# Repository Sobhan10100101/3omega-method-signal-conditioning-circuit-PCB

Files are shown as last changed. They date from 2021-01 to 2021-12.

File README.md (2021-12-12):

3ω method is the most accurate method to investigate the thermal properties of thin films and bulk materials. Howerver, detection of small voltage variation at the third harmonic needs appropriate signal conditioning circuit to:

1. eliminate the 1st harmonic voltage from the responses which can overload the inputs of the lock-in amplifier
2. Amplify the signals before transferring with long cables to prevent distortion 

A simplified schematic diagram is depicted here:


The detailed description of the circuit and implementation of the experiment is published as **Determination of thermal conductivity, thermal diffusivity and specific heat capacity of porous silicon thin films using the 3ω method** which can be found here: https://authors.elsevier.com/a/1eD-044xa8rMx

Here you can find the image of the final PCB:
BlueBird

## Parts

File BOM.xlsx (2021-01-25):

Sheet: Sheet1
Partlist exported from C:/OneDrive - The University of Western Australia/PhD/13 - PCB/3-BlueBird/BlueBird_Sch.sch at 6/07/2020 12:08 PM
Part Value Device Package Description ALLIED_NUMBER CATEGORY DESCRIPTION HEIGHT MANUFACTURER MANUFACTURER_NAME MANUFACTURER_PART_NUMBER MPN OPERATING_TEMP PART_STATUS ROHS_COMPLIANT RS_PART_NUMBER RS_PRICE-STOCK SERIES SUB-CATEGORY THERMALLOSS TYPE VALUE VOLTAGE_RATING
C1 0.1uF C_CHIP-0805(2012-METRIC) CAPC2012X110 Capacitor - Generic Capacitor
C2 0.01uF C_CHIP-0805(2012-METRIC) CAPC2012X110 Capacitor - Generic Capacitor
C3 TAJC225M035RNJ TAJC225M035RNJ CAPPM6032X280N Tantalum Capacitors - Solid SMD 35volts 2.2uF 20% Tantalum Capacitors - Solid SMD 35volts 2.2uF 20% 2.8mm AVX TAJC225M035RNJ 1364458P http://uk.rs-online.com/web/p/products/1364458P
C4 TAJC225M035RNJ TAJC225M035RNJ CAPPM6032X280N Tantalum Capacitors - Solid SMD 35volts 2.2uF 20% Tantalum Capacitors - Solid SMD 35volts 2.2uF 20% 2.8mm AVX TAJC225M035RNJ 1364458P http://uk.rs-online.com/web/p/products/1364458P
C5 TMCUB1V105KTRF TMCUB1V105KTRF CAPPM3528X120N Cap Tant Solid 1uF 35V UB CASE 10% (3.5 X 2.8 X 1.2mm) Inward L SMD 3528-12 8.8 Ohm 125C T/R Cap Tant Solid 1uF 35V UB CASE 10% (3.5 X 2.8 X 1.2mm) Inward L SMD 3528-12 8.8 Ohm 125C T/R 1.2mm Vishay TMCUB1V105KTRF 1882061 http://uk.rs-online.com/web/p/products/1882061
C6 TMCUB1V105KTRF TMCUB1V105KTRF CAPPM3528X120N Cap Tant Solid 1uF 35V UB CASE 10% (3.5 X 2.8 X 1.2mm) Inward L SMD 3528-12 8.8 Ohm 125C T/R Cap Tant Solid 1uF 35V UB CASE 10% (3.5 X 2.8 X 1.2mm) Inward L SMD 3528-12 8.8 Ohm 125C T/R 1.2mm Vishay TMCUB1V105KTRF 1882061 http://uk.rs-online.com/web/p/products/1882061
C7 0.1uF C_CHIP-0805(2012-METRIC) CAPC2012X110 Capacitor - Generic Capacitor
C8 0.1uF C_CHIP-0805(2012-METRIC) CAPC2012X110 Capacitor - Generic Capacitor
C9 0.01uF C_CHIP-0805(2012-METRIC) CAPC2012X110 Capacitor - Generic Capacitor
C10 0.1uF C_CHIP-0805(2012-METRIC) CAPC2012X110 Capacitor - Generic Capacitor
C11 0.1uF C_CHIP-0805(2012-METRIC) CAPC2012X110 Capacitor - Generic Capacitor
C12 0.1uF C_CHIP-0805(2012-METRIC) CAPC2012X110 Capacitor - Generic Capacitor
F1 0458001.DR 0458001.DR FUSC3215X58N LITTELFUSE - 0458001.DR - Fuse, Surface Mount, 1 A, 48 VAC, 63 VDC, Very Fast Acting, 1206 LITTELFUSE - 0458001.DR - Fuse, Surface Mount, 1 A, 48 VAC, 63 VDC, Very Fast Acting, 1206 0.58mm LITTELFUSE 0458001.DR
F2 0458001.DR 0458001.DR FUSC3215X58N LITTELFUSE - 0458001.DR - Fuse, Surface Mount, 1 A, 48 VAC, 63 VDC, Very Fast Acting, 1206 LITTELFUSE - 0458001.DR - Fuse, Surface Mount, 1 A, 48 VAC, 63 VDC, Very Fast Acting, 1206 0.58mm LITTELFUSE 0458001.DR
IC1 OPA2277PA OPA2277PA DIP794W53P254L959H508Q8N Dual precision op-amp,OPA2277PA DIP8 Texas Instruments OPA2277PA, Dual Op Amp, 1MHz, 8-Pin PDIP Dual precision op-amp,OPA2277PA DIP8 Texas Instruments OPA2277PA, Dual Op Amp, 1MHz, 8-Pin PDIP 5.08mm Texas Instruments OPA2277PA 3071673P http://uk.rs-online.com/web/p/products/3071673P
IC2 L7809CV L7809CV TO255P460X1020X2008-3P Standard Regulator 9V 1.5A STMicroelectronics L7809CV, Single Linear Voltage Regulator, 1.5A 9 V, 2%, 3-Pin TO-220 70013895 Standard Regulator 9V 1.5A STMicroelectronics L7809CV, Single Linear Voltage Regulator, 1.5A 9 V, 2%, 3-Pin TO-220 4.6mm STMicroelectronics L7809CV 7140666P http://uk.rs-online.com/web/p/products/7140666P
IC3 KA7909TU KA7909TU TO254P470X1016X2019-3P ON Semiconductor, -9 V Linear Voltage Regulator, 1A, 1-Channel Negative, +/-4% 3-Pin, TO-220 KA7909TU ON Semiconductor, -9 V Linear Voltage Regulator, 1A, 1-Channel Negative, +/-4% 3-Pin, TO-220 KA7909TU 4.7mm ON Semiconductor KA7909TU 7390552P http://uk.rs-online.com/web/p/products/7390552P
IC4 OPA2277PA OPA2277PA DIP794W53P254L959H508Q8N Dual precision op-amp,OPA2277PA DIP8 Texas Instruments OPA2277PA, Dual Op Amp, 1MHz, 8-Pin PDIP Dual precision op-amp,OPA2277PA DIP8 Texas Instruments OPA2277PA, Dual Op Amp, 1MHz, 8-Pin PDIP 5.08mm Texas Instruments OPA2277PA 3071673P http://uk.rs-online.com/web/p/products/3071673P
IC5 OPA2277PA OPA2277PA DIP794W53P254L959H508Q8N Dual precision op-amp,OPA2277PA DIP8 Texas Instruments OPA2277PA, Dual Op Amp, 1MHz, 8-Pin PDIP Dual precision op-amp,OPA2277PA DIP8 Texas Instruments OPA2277PA, Dual Op Amp, 1MHz, 8-Pin PDIP 5.08mm Texas Instruments OPA2277PA 3071673P http://uk.rs-online.com/web/p/products/3071673P
J1 790-1098 790-1098 7901098 2 Way PCB Terminal Strip 2 Way PCB Terminal Strip 8.5mm RS Components 790-1098
J2 790-1098 790-1098 7901098 2 Way PCB Terminal Strip 2 Way PCB Terminal Strip 8.5mm RS Components 790-1098
J3 790-1098 790-1098 7901098 2 Way PCB Terminal Strip 2 Way PCB Terminal Strip 8.5mm RS Components 790-1098
J4 790-1098 790-1098 7901098 2 Way PCB Terminal Strip 2 Way PCB Terminal Strip 8.5mm RS Components 790-1098
J5 790-1098 790-1098 7901098 2 Way PCB Terminal Strip 2 Way PCB Terminal Strip 8.5mm RS Components 790-1098
J6 1729034 1729034 SHDR4W110P0X500_1X4_2000X810X1 Low profile PCB terminal block,5mm,4 way Phoenix Contact COMBICON MKDSN Series 5mm Pitch Straight PCB Terminal Block with Screw Termination, Through Hole, 4 Way 70054377 Low profile PCB terminal block,5mm,4 way Phoenix Contact COMBICON MKDSN Series 5mm Pitch Straight PCB Terminal Block with Screw Termination, Through Hole, 4 Way 10mm Phoenix Contact 1729034 8020620 http://uk.rs-online.com/web/p/products/8020620
J7 1729034 1729034 SHDR4W110P0X500_1X4_2000X810X1 Low profile PCB terminal block,5mm,4 way Phoenix Contact COMBICON MKDSN Series 5mm Pitch Straight PCB Terminal Block with Screw Termination, Through Hole, 4 Way 70054377 Low profile PCB terminal block,5mm,4 way Phoenix Contact COMBICON MKDSN Series 5mm Pitch Straight PCB Terminal Block with Screw Termination, Through Hole, 4 Way 10mm Phoenix Contact 1729034 8020620 http://uk.rs-online.com/web/p/products/8020620
J8 790-1098 790-1098 7901098 2 Way PCB Terminal Strip 2 Way PCB Terminal Strip 8.5mm RS Components 790-1098
J9 790-1098 790-1098 7901098 2 Way PCB Terminal Strip 2 Way PCB Terminal Strip 8.5mm RS Components 790-1098
J10 790-1098 790-1098 7901098 2 Way PCB Terminal Strip 2 Way PCB Terminal Strip 8.5mm RS Components 790-1098
J11 790-1098 790-1098 7901098 2 Way PCB Terminal Strip 2 Way PCB Terminal Strip 8.5mm RS Components 790-1098
J12 R25-3001602 R25-3001602 R253001602 Standoffs & Spacers M2.5 x 16mm HEX M/F BRASS 4.9mm A/F Standoffs & Spacers M2.5 x 16mm HEX M/F BRASS 4.9mm A/F 16mm Harwin R25-3001602
J13 R25-3001602 R25-3001602 R253001602 Standoffs & Spacers M2.5 x 16mm HEX M/F BRASS 4.9mm A/F Standoffs & Spacers M2.5 x 16mm HEX M/F BRASS 4.9mm A/F 16mm Harwin R25-3001602
J14 R25-3001602 R25-3001602 R253001602 Standoffs & Spacers M2.5 x 16mm HEX M/F BRASS 4.9mm A/F Standoffs & Spacers M2.5 x 16mm HEX M/F BRASS 4.9mm A/F 16mm Harwin R25-3001602
L1 MPZ2012S331AT000 MPZ2012S331AT000 INDC2012X105N Ferrite Beads Multi-Layer Power 330Ohm 25% 100MHz 2.5A 50mOhm DCR 0805 T/R Ferrite Beads Multi-Layer Power 330Ohm 25% 100MHz 2.5A 50mOhm DCR 0805 T/R 1.05mm TDK MPZ2012S331AT000
L2 MPZ2012S331AT000 MPZ2012S331AT000 INDC2012X105N Ferrite Beads Multi-Layer Power 330Ohm 25% 100MHz 2.5A 50mOhm DCR 0805 T/R Ferrite Beads Multi-Layer Power 330Ohm 25% 100MHz 2.5A 50mOhm DCR 0805 T/R 1.05mm TDK MPZ2012S331AT000
L3 MPZ2012S331AT000 MPZ2012S331AT000 INDC2012X105N Ferrite Beads Multi-Layer Power 330Ohm 25% 100MHz 2.5A 50mOhm DCR 0805 T/R Ferrite Beads Multi-Layer Power 330Ohm 25% 100MHz 2.5A 50mOhm DCR 0805 T/R 1.05mm TDK MPZ2012S331AT000
L4 MPZ2012S331AT000 MPZ2012S331AT000 INDC2012X105N Ferrite Beads Multi-Layer Power 330Ohm 25% 100MHz 2.5A 50mOhm DCR 0805 T/R Ferrite Beads Multi-Layer Power 330Ohm 25% 100MHz 2.5A 50mOhm DCR 0805 T/R 1.05mm TDK MPZ2012S331AT000
L5 MPZ2012S331AT000 MPZ2012S331AT000 INDC2012X105N Ferrite Beads Multi-Layer Power 330Ohm 25% 100MHz 2.5A 50mOhm DCR 0805 T/R Ferrite Beads Multi-Layer Power 330Ohm 25% 100MHz 2.5A 50mOhm DCR 0805 T/R 1.05mm TDK MPZ2012S331AT000
L6 MPZ2012S331AT000 MPZ2012S331AT000 INDC2012X105N Ferrite Beads Multi-Layer Power 330Ohm 25% 100MHz 2.5A 50mOhm DCR 0805 T/R Ferrite Beads Multi-Layer Power 330Ohm 25% 100MHz 2.5A 50mOhm DCR 0805 T/R 1.05mm TDK MPZ2012S331AT000
LED1 LS_R976 LS_R976 LEDC2012X40N Red 0805 CHIPLED LS R976N-R102 Osram Opto LS R976, CHIPLED 0805 Series Red LED, 633 nm, 2012 (0805), Rectangle Lens SMD Package Red 0805 CHIPLED LS R976N-R102 Osram Opto LS R976, CHIPLED 0805 Series Red LED, 633 nm, 2012 (0805), Rectangle Lens SMD Package 0.4mm OSRAM LS R976 4974804P http://uk.rs-online.com/web/p/products/4974804P
LED2 LS_R976 LS_R976 LEDC2012X40N Red 0805 CHIPLED LS R976N-R102 Osram Opto LS R976, CHIPLED 0805 Series Red LED, 633 nm, 2012 (0805), Rectangle Lens SMD Package Red 0805 CHIPLED LS R976N-R102 Osram Opto LS R976, CHIPLED 0805 Series Red LED, 633 nm, 2012 (0805), Rectangle Lens SMD Package 0.4mm OSRAM LS R976 4974804P http://uk.rs-online.com/web/p/products/4974804P
R1 10K R-US_R0402 R0402 RESISTOR, American symbol
R2 10K R-US_R0402 R0402 RESISTOR, American symbol
R3 10K R-US_R0402 R0402 RESISTOR, American symbol
R4 10K R-US_R0402 R0402 RESISTOR, American symbol
R5 10K R-US_R0402 R0402 RESISTOR, American symbol
R6 10K R-US_R0402 R0402 RESISTOR, American symbol
R7 10K R-US_R0402 R0402 RESISTOR, American symbol
R8 10K R-US_R0402 R0402 RESISTOR, American symbol
R9 5.6K R-US_R0402 R0402 RESISTOR, American symbol
R10 5.6K R-US_R0402 R0402 RESISTOR, American symbol
R11 200 R-US_R0402 R0402 RESISTOR, American symbol
R12 10K R-US_R0402 R0402 RESISTOR, American symbol
R13 10K R-US_R0402 R0402 RESISTOR, American symbol
R14 10K R-US_R0402 R0402 RESISTOR, American symbol
R15 10K R-US_R0402 R0402 RESISTOR, American symbol
R16 10K R-US_R0402 R0402 RESISTOR, American symbol
R17 100 R-US_R0402 R0402 RESISTOR, American symbol
R18 10K R-US_R0402 R0402 RESISTOR, American symbol
R19 50K R-US_R0402 R0402 RESISTOR, American symbol
R20 10K R-US_R0402 R0402 RESISTOR, American symbol
R21 100K R-US_R0402 R0402 RESISTOR, American symbol
R22 100K R-US_R0402 R0402 RESISTOR, American symbol
R23 10K R-US_R0402 R0402 RESISTOR, American symbol
R24 10K R-US_R0402 R0402 RESISTOR, American symbol
R25 10K R-US_R0402 R0402 RESISTOR, American symbol
R26 100K R-US_R0402 R0402 RESISTOR, American symbol
R27 100K R-US_R0402 R0402 RESISTOR, American symbol

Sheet: Sheet2
Parts | comment | Values | Type | Mfr. Part No. | RS Part number | Needed X | Order
Capacitors |  | 0.1 uF | Ceramic |  | 264-4416 | 6 | 25
Capacitors |  | 0.01 uF | Ceramic |  | 298-9309 | 2 | 25
Capacitors |  | 2.2µF | Tantalum |  | 136-4445 | 2 | 20
Capacitors |  | 1uF | Tantalum |  | 188-2380 | 2 | 10
Resistor |  | 0 | 1% |  | 740-9066 | 10 | 50
Resistor |  | 10K | 0.10% |  | 638-0532 | 18 | 50
Resistor |  | 5.6K | 1% |  | 678-9475 | 2 | 50
Resistor |  | 50K | 1% |  | 566-301 | 1 | 5
Resistor |  | 100K | 1% |  | 391-5719 | 3 | 10
Fuse |  |  |  |  | 174-0666 | 2
Ferit Bead |  |  |  |  | 724-1532 | 6 | 25
LED |  | Red |  |  | 497-4804 | 2 | 5
Standoff |  | 2.5M | Male to Female |  | 176-8401 (https://au.rs-online.com/web/p/standoffs/1768401/) | 3 | 10
Washer |  | 2.5M |  |  | 528-160 (https://au.rs-online.com/web/p/tap-washers/0528160/) | 3 | 50
Nut |  | 2.5M |  |  | 122-4399 (https://au.rs-online.com/web/p/hex-nuts/1224399/) | 3 | 50
Spacer |  | M3 |  |  | 102-6384
Terminal |  | 2Way |  |  | 790-1098 | 9 | 5
Terminal |  | 4Way |  | 282836-4 | 361-7689 | 2 | 5
Regulators |  | 9 Volt |  |  | 516-4812 | 1 | 10
Regulators |  | Negative 9 Volt |  |  | 697-4370 | 1 | 5
BNC Connector |  |  |  |  | 512-1225 | 2 | 3
POT1
POT2

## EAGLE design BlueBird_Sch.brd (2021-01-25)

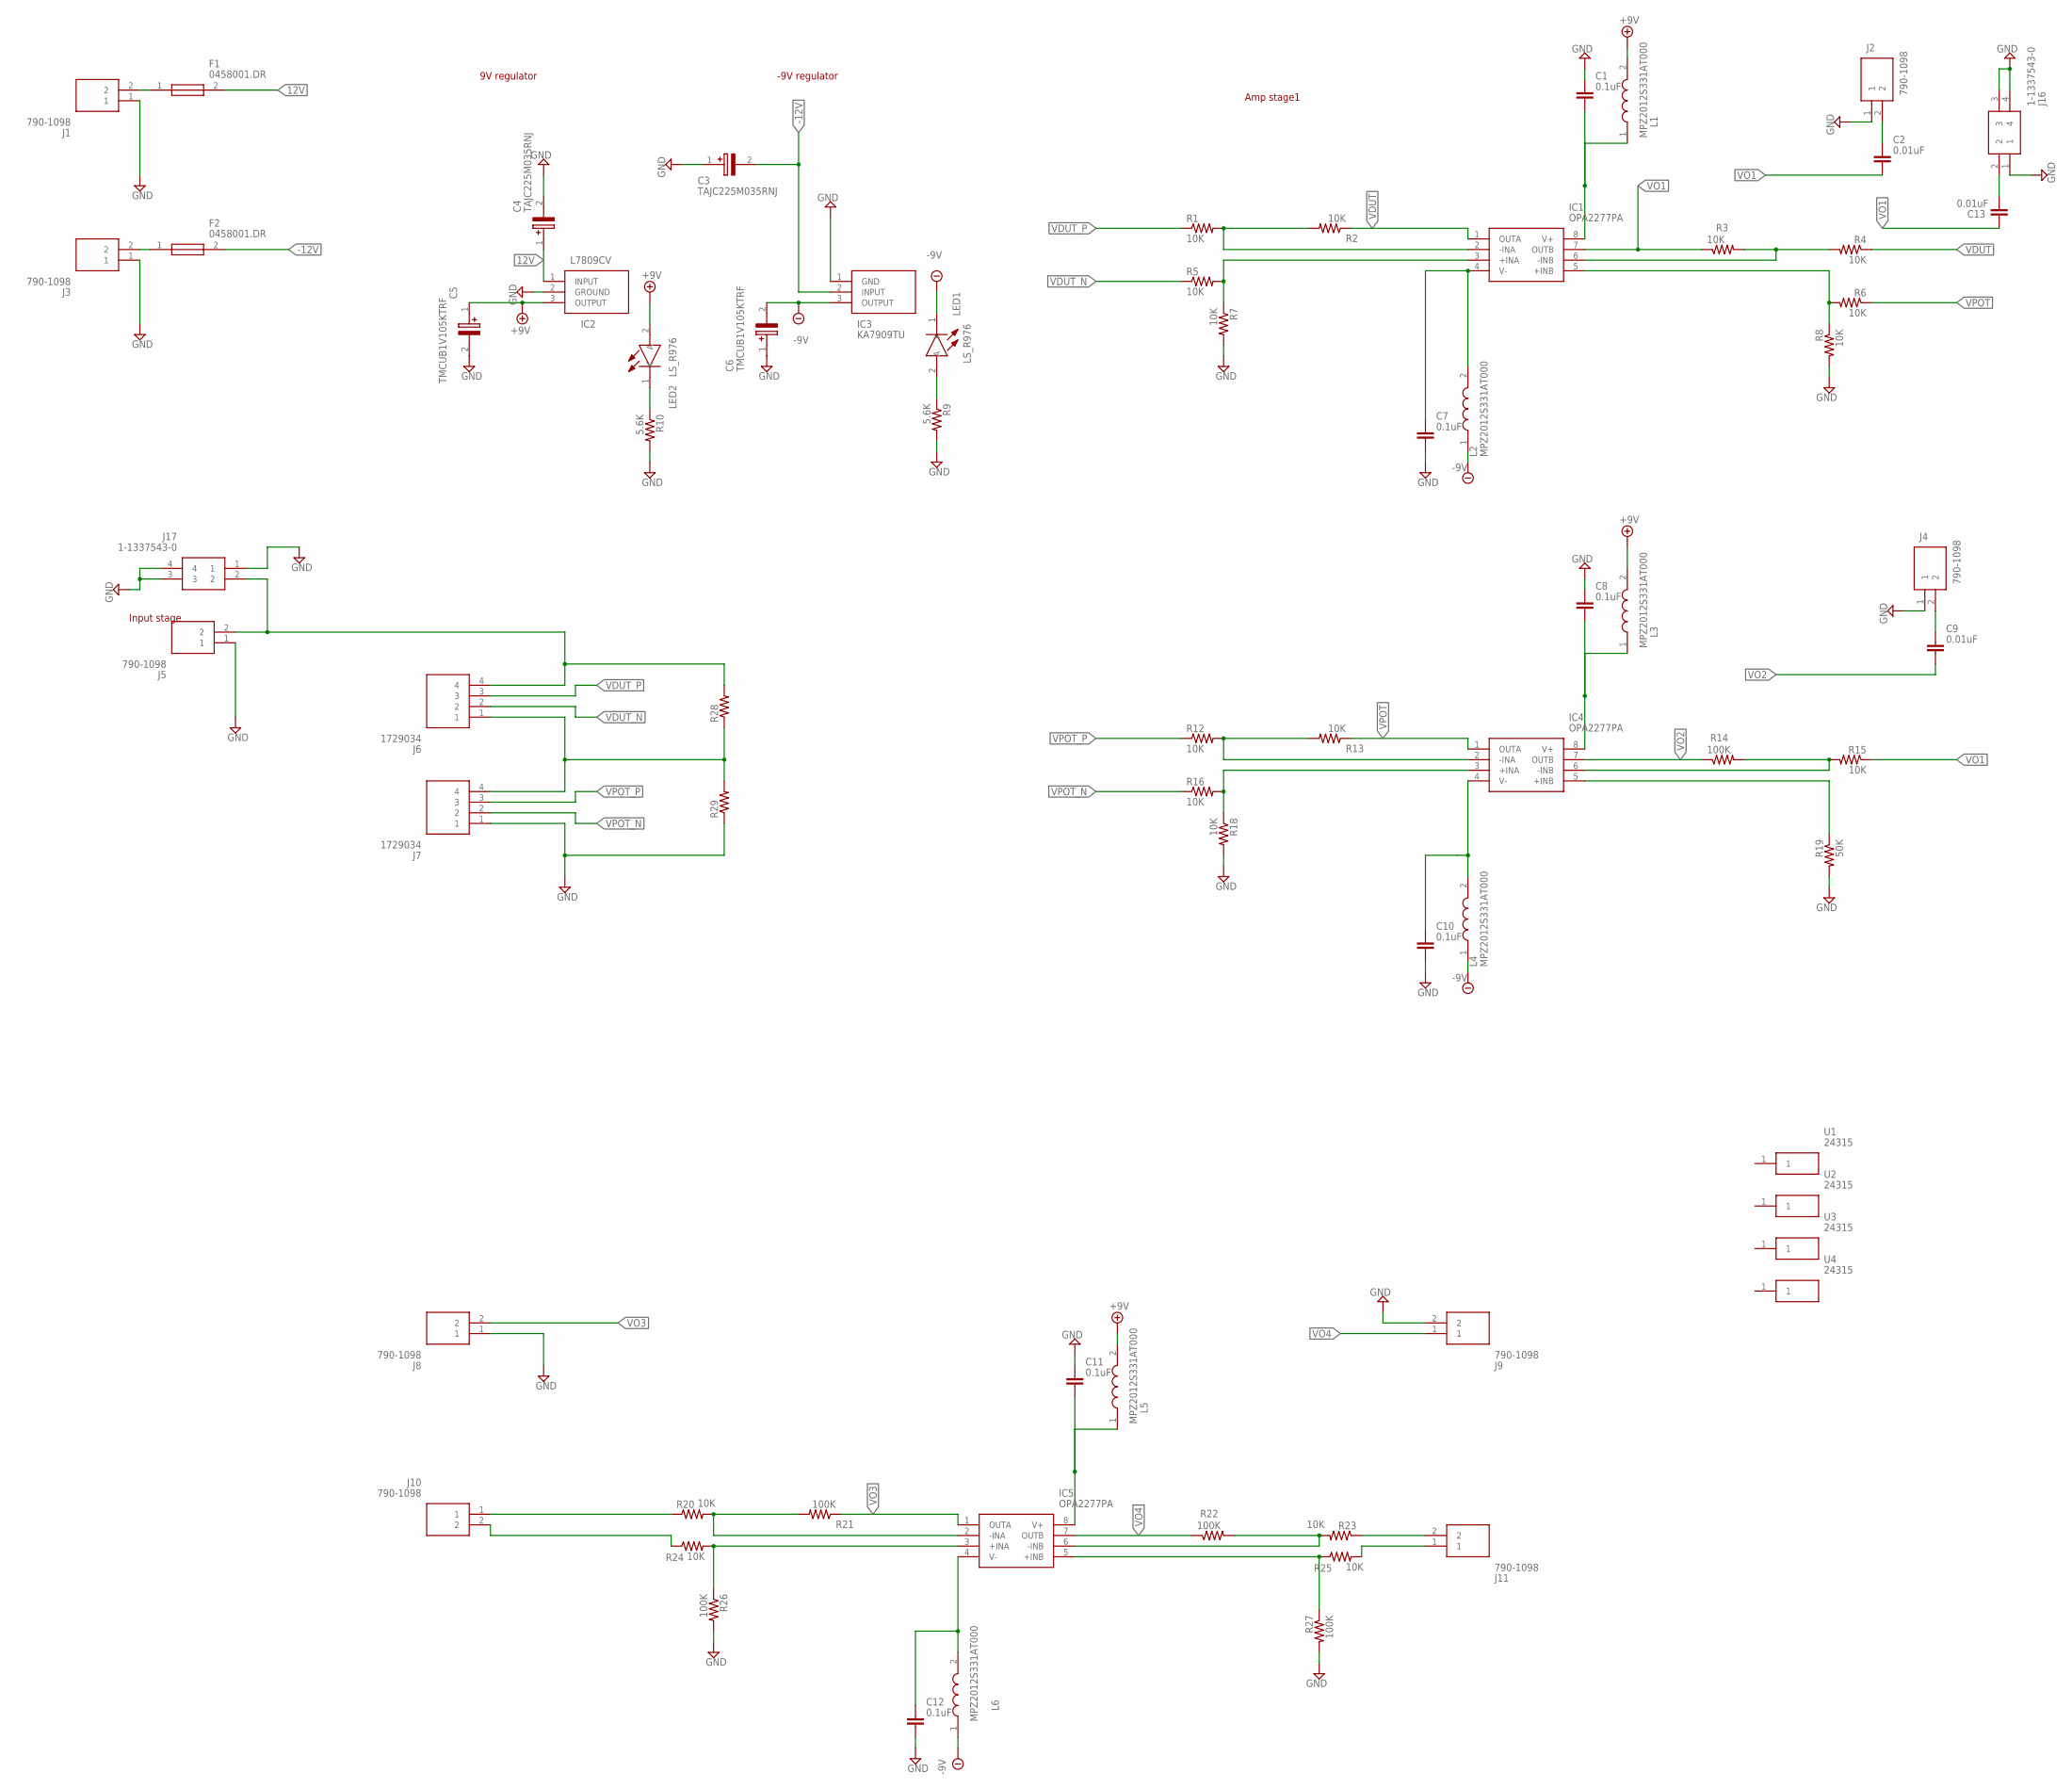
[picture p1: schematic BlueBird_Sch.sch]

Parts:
C1, C7, C8, C10, C11, C12: 0.1uF; CAPC2012X110
C2, C9, C13: 0.01uF; CAPC2012X110
C3, C4: TAJC225M035RNJ; CAPPM6032X280N
C5, C6: TMCUB1V105KTRF; CAPPM3528X120N
F1, F2: 0458001.DR; FUSC3215X58N
IC1, IC4, IC5: OPA2277PA; DIP794W53P254L959H508Q8N
IC2: L7809CV; TO255P460X1020X2008-3P
IC3: KA7909TU; TO254P470X1016X2019-3P
J1, J2, J3, J4, J5, J8, J9, J10, J11: 790-1098; 7901098
J6, J7: 1729034; SHDR4W110P0X500_1X4_2000X810X1
J16, J17: 1-1337543-0
L1, L2, L3, L4, L5, L6: MPZ2012S331AT000; INDC2012X105N
LED1, LED2: LS_R976; LEDC2012X40N
R1, R2, R3, R4, R5, R6, R7, R8, R12, R13, R15, R16, R18, R20, R23, R24, R25: 10K; R0805
R9, R10: 5.6K; R0805
R14, R21, R22, R26, R27: 100K; R0805
R19: 50K; R0805
R28, R29: R-US_R1206; R1206
U1, U2, U3, U4: 24315

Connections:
12V: C4.1 (+), F1.2, IC2.1 (INPUT)
+9V: C5.1 (+), IC2.3 (OUTPUT), L1.2, L3.2, L5.2, LED2.2 (A)
-9V: C6.2 (-), IC3.3 (OUTPUT), L2.1, L4.1, L6.1, LED1.1 (K)
-12V: C3.2 (-), F2.2, IC3.2 (INPUT)
GND: C1.1, C3.1 (+), C4.2 (-), C5.2 (-), C6.1 (+), C7.2, C8.1, C10.2, C11.1, C12.2, IC2.2 (GROUND), IC3.1 (GND), J1.1, J2.1, J3.1, J4.1, J5.1, J7.1, J8.1, J9.2, J16.1, J16.3, J16.4, J17.1, J17.3, J17.4, R7.2, R8.2, R9.2, R10.2, R18.2, R19.2, R26.2, R27.2, R29.1
unnamed: F1.1, J1.2
unnamed: F2.1, J3.2
unnamed: C7.1, IC1.4 (V-), L2.2
unnamed: J10.2, R24.1
unnamed: J10.1, R20.1
unnamed: J5.2, J6.4, J17.2, R28.2
unnamed: J11.2, R23.1
unnamed: J11.1, R25.2
unnamed: C9.1, J4.2
unnamed: C2.1, J2.2
unnamed: LED1.2 (A), R9.1
unnamed: LED2.1 (K), R10.1
unnamed: C13.1, J16.2
unnamed: J6.1, J7.4, R28.1, R29.2
unnamed: IC1.2 (-INA), R1.2, R2.2
unnamed: IC1.3 (+INA), R5.2, R7.1
unnamed: C8.2, IC4.8 (V+), L3.1
unnamed: C1.2, IC1.8 (V+), L1.1
unnamed: C11.2, IC5.8 (V+), L5.1
unnamed: IC1.6 (-INB), R3.2, R4.2
unnamed: IC1.5 (+INB), R6.2, R8.1
unnamed: C10.1, IC4.4 (V-), L4.2
unnamed: IC4.2 (-INA), R12.2, R13.2
unnamed: IC4.3 (+INA), R16.2, R18.1
unnamed: C12.1, IC5.4 (V-), L6.2
unnamed: IC4.6 (-INB), R14.2, R15.2
unnamed: IC4.5 (+INB), R19.1
unnamed: IC5.2 (-INA), R20.2, R21.2
unnamed: IC5.3 (+INA), R24.2, R26.1
unnamed: IC5.6 (-INB), R22.2, R23.2
unnamed: IC5.5 (+INB), R25.1, R27.1
VDUT: IC1.1 (OUTA), R2.1, R4.1
VDUT_N: J6.2, R5.1
VDUT_P: J6.3, R1.1
VO1: C2.2, C13.2, IC1.7 (OUTB), R3.1, R15.1
VO2: C9.2, IC4.7 (OUTB), R14.1
VO3: IC5.1 (OUTA), J8.2, R21.1
VO4: IC5.7 (OUTB), J9.1, R22.1
VPOT: IC4.1 (OUTA), R6.1, R13.1
VPOT_N: J7.2, R16.1
VPOT_P: J7.3, R12.1

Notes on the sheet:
9V regulator
-9V regulator
Amp stage1
Input stage

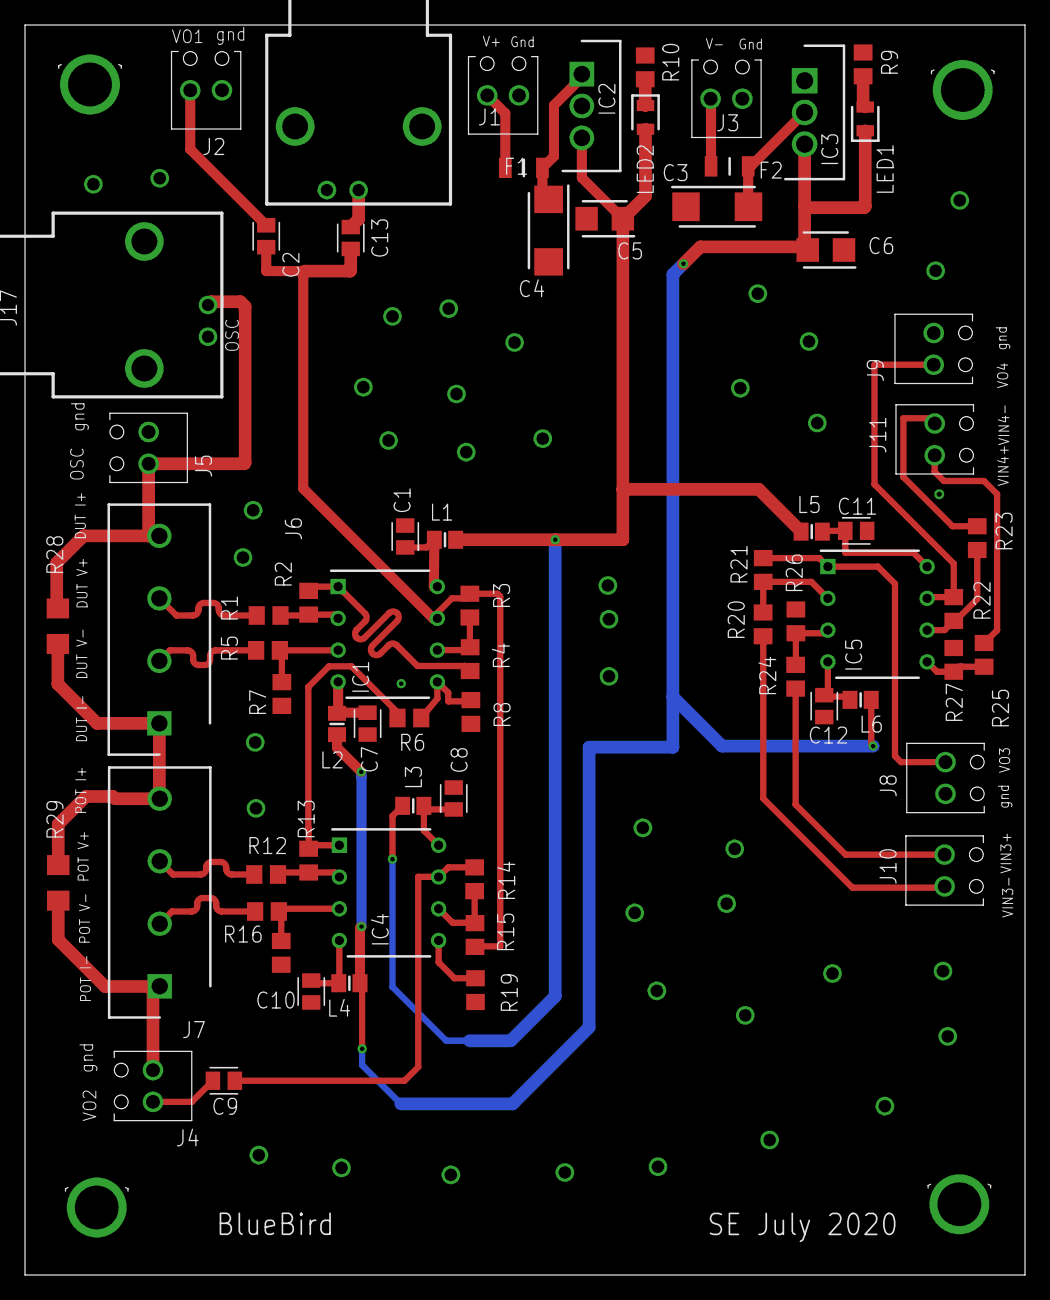
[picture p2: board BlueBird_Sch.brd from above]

Board: 2 copper layers, 80.0 x 100.0 mm, 72 parts (0 on the bottom side), 46 nets.
